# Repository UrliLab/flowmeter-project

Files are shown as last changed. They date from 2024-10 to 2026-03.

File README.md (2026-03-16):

# Urli Lab Pressure-drop Flowmeter

## Authors

- Urli M., Lambert M.-C., and Périé C.

## Info

- **E-mail**: [urli.morgane@uqam.ca](mailto:urli.morgane@uqam.ca)
- **Website**: [https://www.morganeurli.com](https://www.morganeurli.com)

## What is the Flowmeter Project?

This repository provides detailed information on the firmware and software (R Shiny application) required to assemble the electronic box of a pressure-drop flowmeter, adapted from Sack et al. (2011). The flowmeter can be used to measure flow rates based on the pressure drop within a system, and subsequently determine the hydraulic conductivity of various organs (e.g., stem, leaf, or root). Our software is designed for stems but can be modified to accommodate other organs.

Please note that this repository **does not include** the protocol for using the flowmeter or the R Shiny application. These protocols are  available on the Prometheus Protocols website ([Protocole Prometheus](https://wp.me/P9rDtN-15s)).
For further details on the validation of this device, please refer to the peer‑reviewed article demonstrating its accuracy and reliability, available here: [Samson-Tshimbalanga, Périé and Urli (2026) Plant Direct]( https://onlinelibrary.wiley.com/doi/10.1002/pld3.70154).

## Installation

### Electronic Box of the Flowmeter

To assemble the electronic box, follow the instructions provided in the repository, particularly in the `firmware`, `pcb`, and `mechanical` folders.

### Software

The repository includes the software necessary to control and interact with the flowmeter. Make sure to install the following dependencies:

- **R** (version 4.2.1 or higher)
- **Additional libraries**:
  
```r
library(conflicted)
library(shiny)
library(shinyTime)
library(shinydashboard)
library(data.table)
library(shinyjs)
library(tidyverse)
library(DT)
library(shinyFiles)
library(fontawesome)
library(readODS)
library(gridExtra)
library(ggplot2)
library(dplyr)
```

## How to Use

Once the hardware is assembled and the software is installed, you can begin using the flowmeter following the step-by-step usage protocol available once the protocol is published on Prometheus.

## Licence

This repository uses the following licenses:

- **GPL-3.0 License** for the software (including code for controlling the flowmeter and interfacing with the firmware).
- **CC BY-SA License** for the documentation, including assembly instructions and explanatory content.

## Citation

If you use this repository in your research or project, please cite the following:

- Urli, M., Lambert, M.-C., & Périé, C. (2025). *Urli Lab Pressure-drop Flowmeter*. [GitHub Repository]. Available at: [https://github.com/UrliLab/flowmeter-project](https://github.com/UrliLab/flowmeter-project)

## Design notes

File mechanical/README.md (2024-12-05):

# Urli Lab Pressure-drop flow-meter mechanical informations

## Info
- E-mail: urli.morgane@uqam.ca
- Website: https://www.morganeurli.com

The following folder contains information on the materials used to build the box (bill of material file), as well as 3D drawings of the box and the pressure sensor supports.

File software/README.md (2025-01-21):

# Urli Lab Pressure-drop flow-meter mechanical informations

## Info
- E-mail: urli.morgane@uqam.ca
- Website: https://www.morganeurli.com

## Software

The following folder contains the software required to control and interact with the pressure-drop flowmeter. The software is designed using the **R** programming language and utilizes the **R Shiny** framework to provide an interactive application for data visualization and management.

### Software Requirements

To run the software, ensure that you have the following software and packages installed:

- **R** (version 4.2.1 or higher)
- **R Shiny**: This is the primary framework used for building interactive web applications within R.
- The following **R libraries** are required for the application to function:

```r
# List of required libraries
library(conflicted)
library(shiny)
library(shinyTime)
library(shinydashboard)
library(data.table)
library(shinyjs)
library(tidyverse)
library(DT)
library(shinyFiles)
library(fontawesome)
library(readODS)
library(gridExtra)
library(ggplot2)
library(dplyr)
```
For more detailed instructions on how to use the flowmeter and the R Shiny application, refer to the protocol, which is currently under submission to the Prometheus Protocols website (https://prometheusprotocols.net/).

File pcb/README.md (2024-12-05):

# Urli Lab Pressure-drop flow-meter PCB

## Info
- E-mail: urli.morgane@uqam.ca
- Website: https://www.morganeurli.com

The following folder contains the following pcb-related files:
- the bill of material
- gerber files
- the pick and place file
- the box diagram in pdf format
- the assembly order
- internal and external cable diagram

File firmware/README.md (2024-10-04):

# Urli Lab Pressure-drop flow-meter Electronic Box Controller

## Info
- E-mail: urli.morgane@uqam.ca
- Website: https://www.morganeurli.com

## Setup

The following script create and activate a python virtual environnement and install all dependencies.

```shell
python3 -m venv .venv
source .venv/bin/activate
pip install -r requirements.txt
```
## Quickstart

Note: This require PowerShell script execution permission. 

### Flashing Micropython on esp32 device

Download micropython binary from https://micropython.org/resources/firmware/ESP32_GENERIC_S3-20240105-v1.22.1.bin
Press the RESET and BOOT button simultaneously and then release RESET button. The programming serial port should now be available. (See https://docs.espressif.com/projects/esptool/en/latest/esp32/esptool/index.html) 

```shell
python -m esptool --chip auto --port YOUR_COM_PORT erase_flash
python -m esptool --chip auto --port YOUR_COM_PORT write_flash --flash_size detect -z 0 YOUR_PATH_TO_MICROPYTHON_BIN

```
Then, reboot the controller by pressing RESET only. The new COM port should be available.

### Upload Pressure-drop flow-meter source code to the ESP32 MicroPython filesystem
```shell
mpremote connect YOUR_COM_PORT fs cp src/ds18B20.py :
mpremote connect YOUR_COM_PORT fs cp src/honeywell_mpr.py :
mpremote connect YOUR_COM_PORT fs cp src/led.py :
mpremote connect YOUR_COM_PORT fs cp src/main.py :
mpremote connect YOUR_COM_PORT fs cp src/user_button.py :
```

### Enter repl session
```shell
mpremote connect YOUR_COM_PORT
```

### Leaving repl session
Press Ctrl+] keys.

### esp32 soft-reset
In repl session without micropython app code running, then press Ctrl+D keys.

### Removing all files from ESP32 MicroPython filesystem
```shell
mpremote connect YOUR_COM_PORT + exec "import os, uos; [uos.remove(f) for f in os.listdir()]"
```

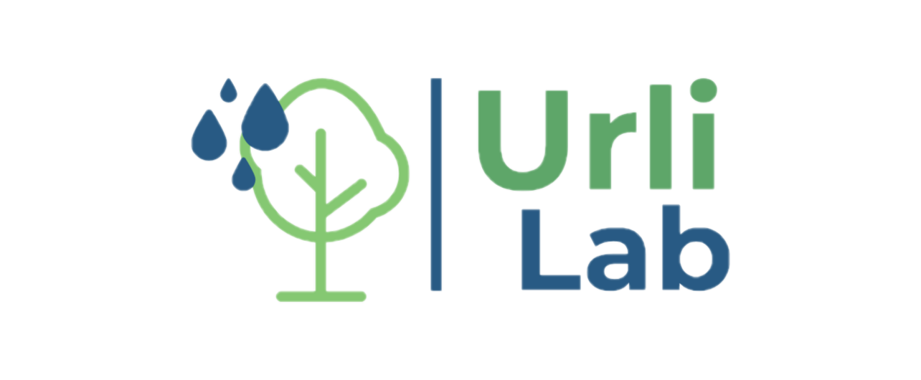
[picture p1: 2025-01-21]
software/www/Twitter Header Photo TR.png

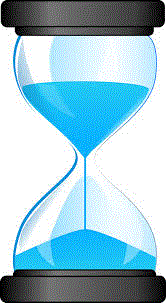
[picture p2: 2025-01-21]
software/www/sablier.gif

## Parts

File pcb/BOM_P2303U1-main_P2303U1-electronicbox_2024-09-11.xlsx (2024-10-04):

No. | Quantity | Comment | Designator | Footprint | Value | Manufacturer Part | Manufacturer | Supplier Part | Supplier
1 | 5 | 100nF | C1,C2,C3,C4,C9 | C0805 | 100nF | CC0805KRX7R9BB104 | YAGEO(国巨) | C49678 | LCSC
2 | 4 | 10uF | C5,C6,C7,C8 | C0805 | 10uF | GRM21BR61H106KE43L | muRata(村田) | C440198 | LCSC
3 | 1 | 22232031 | CN1 | CONN-TH_3P-P2.54_22-23-2031 |  | 22232031 | MOLEX | C234181 | LCSC
4 | 3 | 22232041 | CN2,CN3,CN4 | CONN-TH_4P-P2.54_22232041 |  | 22232041 | MOLEX | C164168 | LCSC
5 | 2 | 22-23-2021 | CN5,CN6 | Molex-22-23-2021-Manufacturer_Recommended | 22-23-2021 | 22232021 | MOLEX | C234180 | LCSC
6 | 1 | SS54 | D1 | SMA_L4.4-W2.8-LS5.4-R-RD |  | SS54 | MDD | C22452 | LCSC
7 | 4 | ESD5B5.0ST1G | D2,D3,D4,D5 | SOD-523_L1.2-W0.8-LS1.6-BI |  | ESD5B5.0ST1G | onsemi(安森美) | C93623 | LCSC
8 | 2 | PM254-1-18-Z-8.5 | H1,H2 | HDR-TH_18P-P2.54-V-F |  | PM254-1-18-Z-8.5 | HCTL(华灿天禄) | C2897381 | LCSC
9 | 1 | NCD0805R1 | LED1 | LED0805-RD_RED |  | NCD0805R1 | 国星光电 | C84256 | LCSC
10 | 1 | SK6812D-EC3210R | LED2 | LED-SMD_4P_SK6812D-EC3210R |  | SK6812D-EC3210R | 欧思科光电 | C2890041 | LCSC
11 | 7 | 10kΩ | R1,R2,R3,R4,R5,R7,R8 | R0805 | 10kΩ | 0805W8F1002T5E | UNI-ROYAL(厚声) | C17414 | LCSC
12 | 2 | 4.7kΩ | R6,R9 | R0805 | 4.7kΩ | 0805W8F4701T5E | UNI-ROYAL(厚声) | C17673 | LCSC
13 | 2 | TS-1187A-B-A-B | SW1,SW2 | SW-SMD_4P-L5.1-W5.1-P3.70-LS6.5-TL-2 |  | TS-1187A-B-A-B | XKB Connectivity(中国星坤) | C318884 | LCSC
14 | 1 | ESP32-S3-WROOM-1-N8 | U1 | WIFIM-SMD_ESP32-S3-WROOM-1-N8 |  | ESP32-S3-WROOM-1-N8 | ESPRESSIF(乐鑫) | C2913198 | LCSC
15 | 1 | AMS1117-3.3 | U2 | SOT-223-3_L6.5-W3.4-P2.30-LS7.0-BR |  | AMS1117-3.3 | AMS | C6186 | LCSC

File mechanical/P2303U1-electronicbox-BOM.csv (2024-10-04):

Manufacturer Part Number | Manufacturer Name | Description | Quantity
SW-R3-1A-A-1-2 | Adam Tech | SUBMINIATURE ROCKER SWITCH, SOLD | 1
RP3502ARED | E-Switch | SWITCH PUSH SPST-NO 3A 120V | 1
NUB-20PMFP-SC7001 | Amphenol LTW | CONN RCP USB2.0 MINI B 5P PCB | 1
T4070014031-001 | TE Connectivity AMP Connectors | CBL 3POS MALE TO WIRE 0.66' | 1
T4070014041-001 | TE Connectivity AMP Connectors | CBL 4POS MALE TO WIRE 0.66' | 2
22013027 | Molex | 900-0022013027-ND | 2
22013037 | Molex | CONN RCPT HSG 3POS 2.54MM | 1
22013047 | Molex | CONN RCPT HSG 4POS 2.54MM | 3
8500113 | Molex | CONN 22-30AWG CRIMP TIN | 19
21348081489010 | HARTING | CBL 4POS MALE TO FMALE 3.28' | 2
21348100388010 | HARTING | CBL 3POS FMALE TO WIRE 3.28' | 1
DFR0198 | DFRobot | WATERPROOF DIGITAL TEMPE | 1
1037N115 | mcmaster-carr | Machine-Mount Corrosion-Resistant Washdown Enclosure with See-Through Cover, 4-3/4" High x 4-3/4" Wide x 2-3/8" Deep | 1
90380A348 | mcmaster-carr | Phillips Rounded Head Thread-Forming Screws for Plastic, Zinc-Plated Steel, M3 Size, 6 mm Long | bag of 100

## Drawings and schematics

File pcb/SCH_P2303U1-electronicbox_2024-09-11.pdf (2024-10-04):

IO0 27 IO35 28 IO36 29 IO37 30 IO38 31 IO39 32 IO40 33 IO41 34 IO42 35 RXD0 36 TXD0 37 IO2 38 IO1 39 GND 40

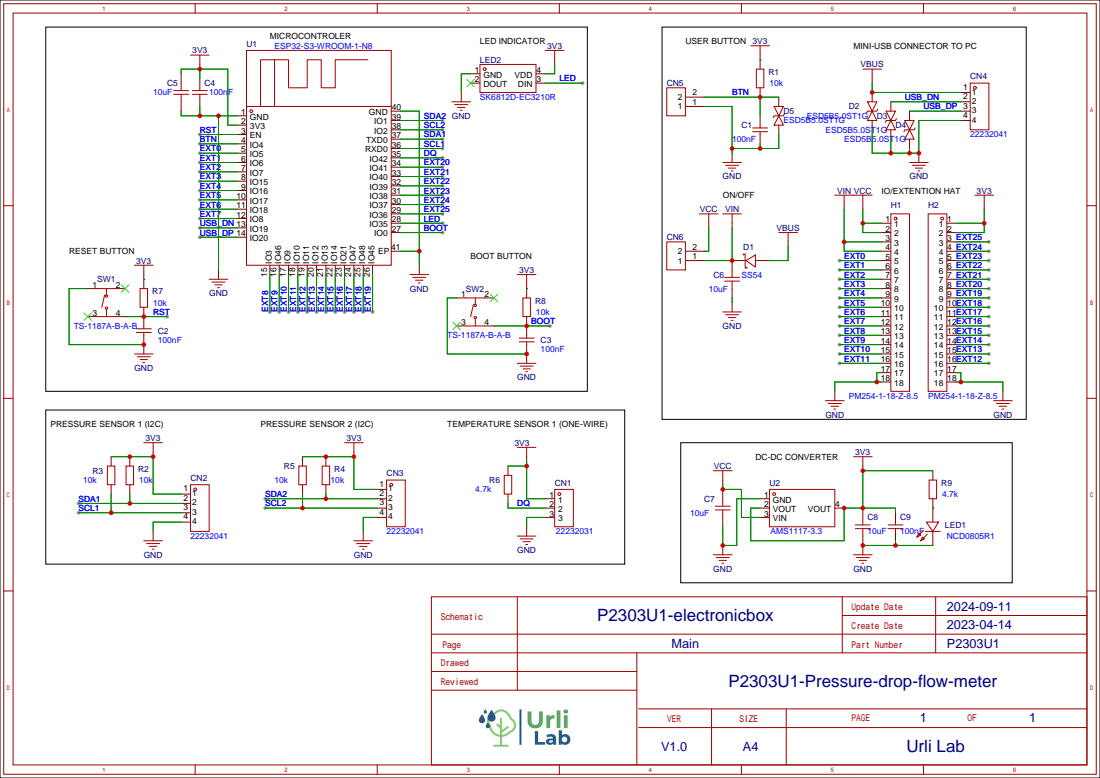
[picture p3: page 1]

MINI-USB CONNECTOR TO PC
VBUS

Main
P2303U1-Pressure-drop-flow-meter

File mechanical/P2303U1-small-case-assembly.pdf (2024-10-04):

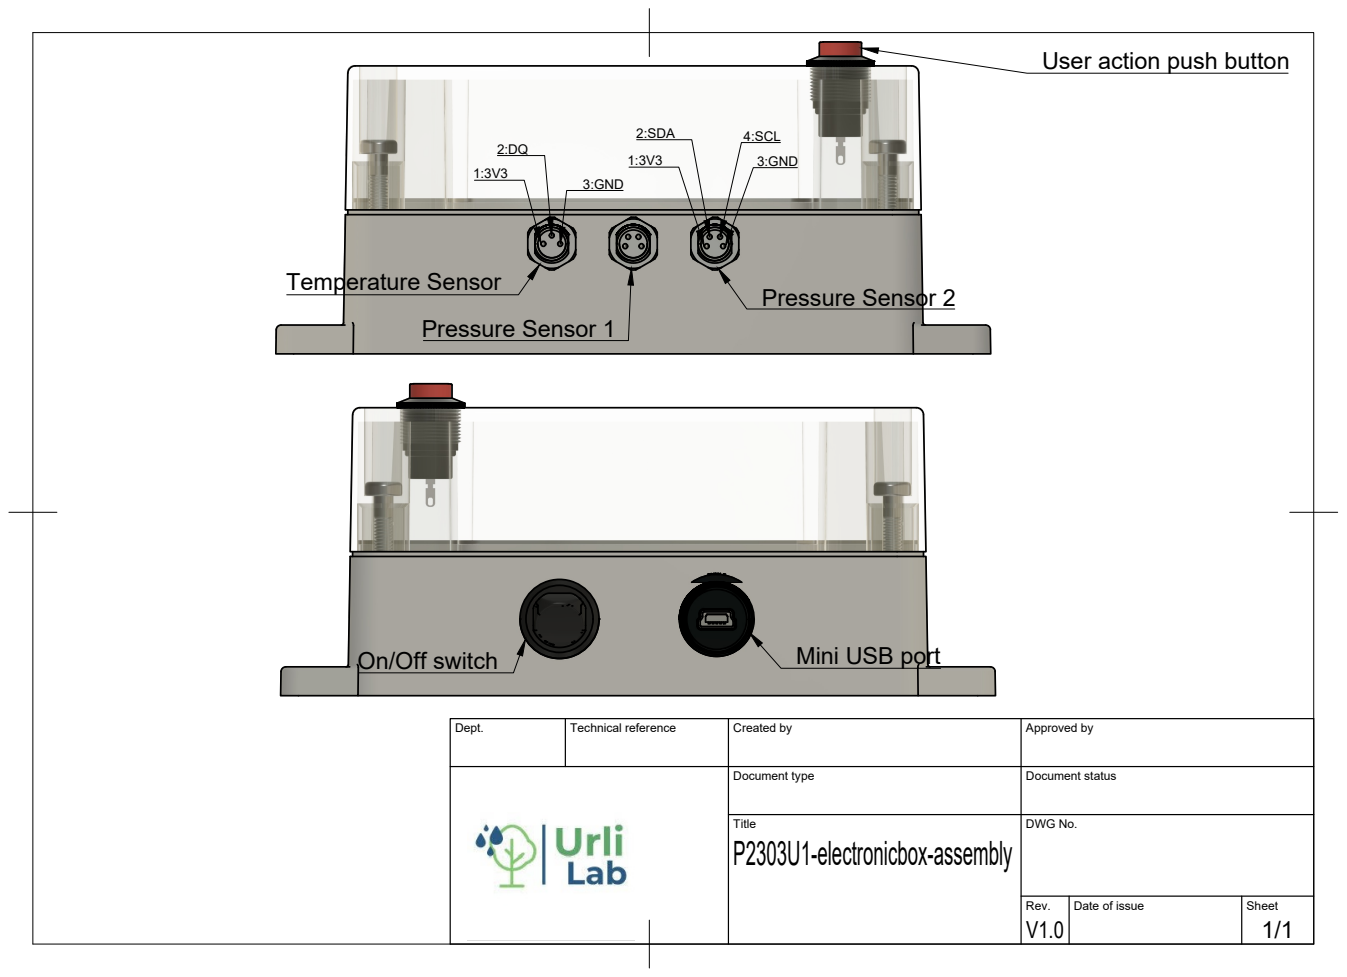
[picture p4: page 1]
On/Off switch; Mini USB port; Temperature Sensor; Pressure Sensor 1; Pressure Sensor 2

User action push button

Dept. | Technical reference | Created by | Approved by

Document type | Document status

Title P2303U1-electronicbox-assembly | DWG No.

Rev. V1.0 | Date of issue | Sheet 1/1

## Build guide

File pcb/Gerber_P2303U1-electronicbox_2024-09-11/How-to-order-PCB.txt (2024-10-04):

How to Order PCB

Please refer to:
https://prodocs.easyeda.com/en/pcb/order-order-pcb/index.html

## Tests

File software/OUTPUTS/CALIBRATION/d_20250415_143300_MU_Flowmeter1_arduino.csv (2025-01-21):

Height | ELTime | Step | P1.psi | P2.psi | T3_oC
5 | 1 | 1 | 0.09117617 | 0.09224454 | 21.9375
5 | 3 | 1 | 0.09154152 | 0.09189181 | 21.9375
5 | 5 | 1 | 0.09161623 | 0.09194939 | 21.9375
5 | 7 | 1 | 0.09161901 | 0.09189046 | 21.9375
5 | 9 | 1 | 0.09161467 | 0.09195602 | 21.9375
5 | 11 | 1 | 0.09160764 | 0.09203303 | 21.9375
5 | 13 | 1 | 0.09162214 | 0.09212734 | 21.9375
5 | 15 | 1 | 0.09161922 | 0.09220326 | 21.9375
5 | 17 | 1 | 0.09158365 | 0.09219012 | 21.9375
5 | 19 | 1 | 0.09158127 | 0.09218655 | 21.9375
5 | 21 | 1 | 0.09128445 | 0.0921415 | 21.9375
10 | 32 | 2 | 0.1614722 | 0.1619935 | 21.9375
10 | 34 | 2 | 0.1615245 | 0.1615608 | 21.9375
10 | 36 | 2 | 0.1615227 | 0.161619 | 22
10 | 38 | 2 | 0.16151 | 0.1615903 | 22
10 | 40 | 2 | 0.1615199 | 0.1616766 | 22
10 | 42 | 2 | 0.1615019 | 0.1616782 | 22
10 | 44 | 2 | 0.1614759 | 0.1617704 | 22
10 | 46 | 2 | 0.1614564 | 0.1615722 | 22
10 | 48 | 2 | 0.161479 | 0.1614748 | 22
10 | 50 | 2 | 0.1614821 | 0.1614305 | 22
10 | 52 | 2 | 0.1614664 | 0.1615326 | 22
10 | 54 | 2 | 0.1614791 | 0.1615158 | 22
10 | 56 | 2 | 0.1610649 | 0.161459 | 22
15 | 74 | 3 | 0.2315209 | 0.2316488 | 22.0625
15 | 76 | 3 | 0.2318989 | 0.2317783 | 22.0625
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

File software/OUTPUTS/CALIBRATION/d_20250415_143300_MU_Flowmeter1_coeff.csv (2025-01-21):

Variable | P1 | P2
adj.r.squared (R2 > 0.999) | 0.999997505325253 | 0.999996521778103
Intercept | -0.00147591066195798 | -0.00149508122407258
Slope | 0.0710405358530191 | 0.0710702964986561

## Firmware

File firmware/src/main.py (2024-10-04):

import sys
import time
from machine import SoftI2C, Pin

import machine
machine.freq(240000000)

import led
import uasyncio as asyncio

# Initialize the LED status indicator
status = led.LED(Pin(35), 100, led.Colors.YELLOW)

# Initialize global variables
step = 0
measure_lock = asyncio.Lock()
timer_offset = time.ticks_ms()
measurement_period_ms = 2000
measuring = False

try:
    # Import the Honeywell MPR sensor library
    import honeywell_mpr

    # Initialize I2C interfaces for pressure sensors
    i2c_pressure_1 = SoftI2C(scl=Pin(44), sda=Pin(43), freq=100000)
    i2c_pressure_2 = SoftI2C(scl=Pin(2), sda=Pin(1), freq=100000)

    pressure_sensor_1 = honeywell_mpr.MprSensor(i2c_pressure_1, 
                                                transfer_function=honeywell_mpr.transfer_function_c, 
                                                pressure_range=(0.0,1.0),
                                                label="pressure_1")
    pressure_sensor_2 = honeywell_mpr.MprSensor(i2c_pressure_2, 
                                                transfer_function=honeywell_mpr.transfer_function_c, 
                                                pressure_range=(0.0,1.0),
                                                label="pressure_2")
    
    from ds18B20 import DS18B20

    temperature_sensor_1 = DS18B20(data_pin=Pin(42))

    # Import and initialize the user button
    from user_button import UserButton

    button = UserButton(Pin(4))

    # Coroutine to handle long press events
    async def on_long_press_event():
        global step, timer_offset, measure_lock, measuring
        while True:
            await button.long_press_event.wait()
            status.set_color(led.Colors.MAGENTA)
            step = 0
            if measuring:
                await measure_lock.acquire()
                measuring = False
            await asyncio.sleep(1)
            status.set_color(led.Colors.GREEN)

    # Coroutine to handle short press events
    async def on_short_press_event():
        global step, measure_lock, measuring, timer_offset
        while True:
            await button.short_press_event.wait()
            if measuring:
                await measure_lock.acquire()
                status.set_color(led.Colors.GREEN)
            else:
                step += 1
                if step == 1:
                    timer_offset = time.ticks_ms()
                measure_lock.release()
                status.set_color(led.Colors.BLUE)
            measuring = not measuring

    # Main coroutine
    async def main():
        await measure_lock.acquire()

        # Create tasks for button press events
        asyncio.create_task(on_long_press_event())
        asyncio.create_task(on_short_press_event())

        status.set_color(led.Colors.GREEN)

        while True:
            async with measure_lock:
                t = time.ticks_ms()
                # Gather measurements from sensors
                values = await asyncio.gather(
                    pressure_sensor_1.get_measurement(100),
                    pressure_sensor_2.get_measurement(100),
                    temperature_sensor_1.get_measurement(),
                )
                pressure_1 = values[0]
                pressure_2 = values[1]
                temperature_3 = values[2]

                tab_separed_values = '\t'.join([str(value) for value in [time.ticks_diff(time.ticks_ms(),timer_offset)//1000,
                                                                        step,
                                                                        pressure_1,
                                                                        pressure_2,
                                                                        temperature_3]])
                print(tab_separed_values)

                # Sleep for the remaining measurement period
                await asyncio.sleep_ms(
                    max(0, measurement_period_ms - time.ticks_diff(time.ticks_ms(), t))
                )

    # Run the main coroutine
    asyncio.run(main())

except Exception as e:
    # Handle exceptions and set LED to red
    sys.print_exception(e)
    status.set_color(led.Colors.RED)

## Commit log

2024-10-04 add mechanical
    [P2303U1-electronicbox-BOM.csv]
2024-10-04 add pcb and mechanical
    [BOM_P2303U1-main_P2303U1-electronicbox_2024-09-11.xlsx, Drill_PTH_Through.DRL, Drill_PTH_Through_Via.DRL, Gerber_BoardOutlineLayer.GKO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]
2025-01-21 new version of software
    [01_peekmeasurement.csv, 02_peekmeasurement.csv, 03_peekmeasurement.csv, DB.csv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]
2025-01-21 new version of software folder
    [01_peekmeasurement.csv, 02_peekmeasurement.csv, 03_peekmeasurement.csv, DB.csv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]
2025-05-04 Add files via upload
    Add a new version of software directory
    [01_PEEKmeasurement.csv, 02_PEEKmeasurement.csv, 03_PEEKmeasurement.csv, DB.csv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]
2025-05-04 Add files via upload
    Create new software directory.
    [01_PEEKmeasurement.csv, 02_PEEKmeasurement.csv, 03_PEEKmeasurement.csv, DB.csv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]
2025-06-03 Fix error in Peek-tube calibration
    Fix error in Peek-tube calibration: corrected formula to convert lab-measured conductance to reference conductance at 25°C
2025-08-27 fix temperature correction
2025-08-27 fix error
    [PEEK_tubing_PEEKid.csv]
